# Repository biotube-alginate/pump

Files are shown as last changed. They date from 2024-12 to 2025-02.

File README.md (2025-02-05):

# Overview
This is the pump we used in BioTube for extruding alginate solution of high concentration (4%) and thus high viscocity. The noozle of the syringe can be directly vertically put into a Calcium solution bath without extra tubing connections.

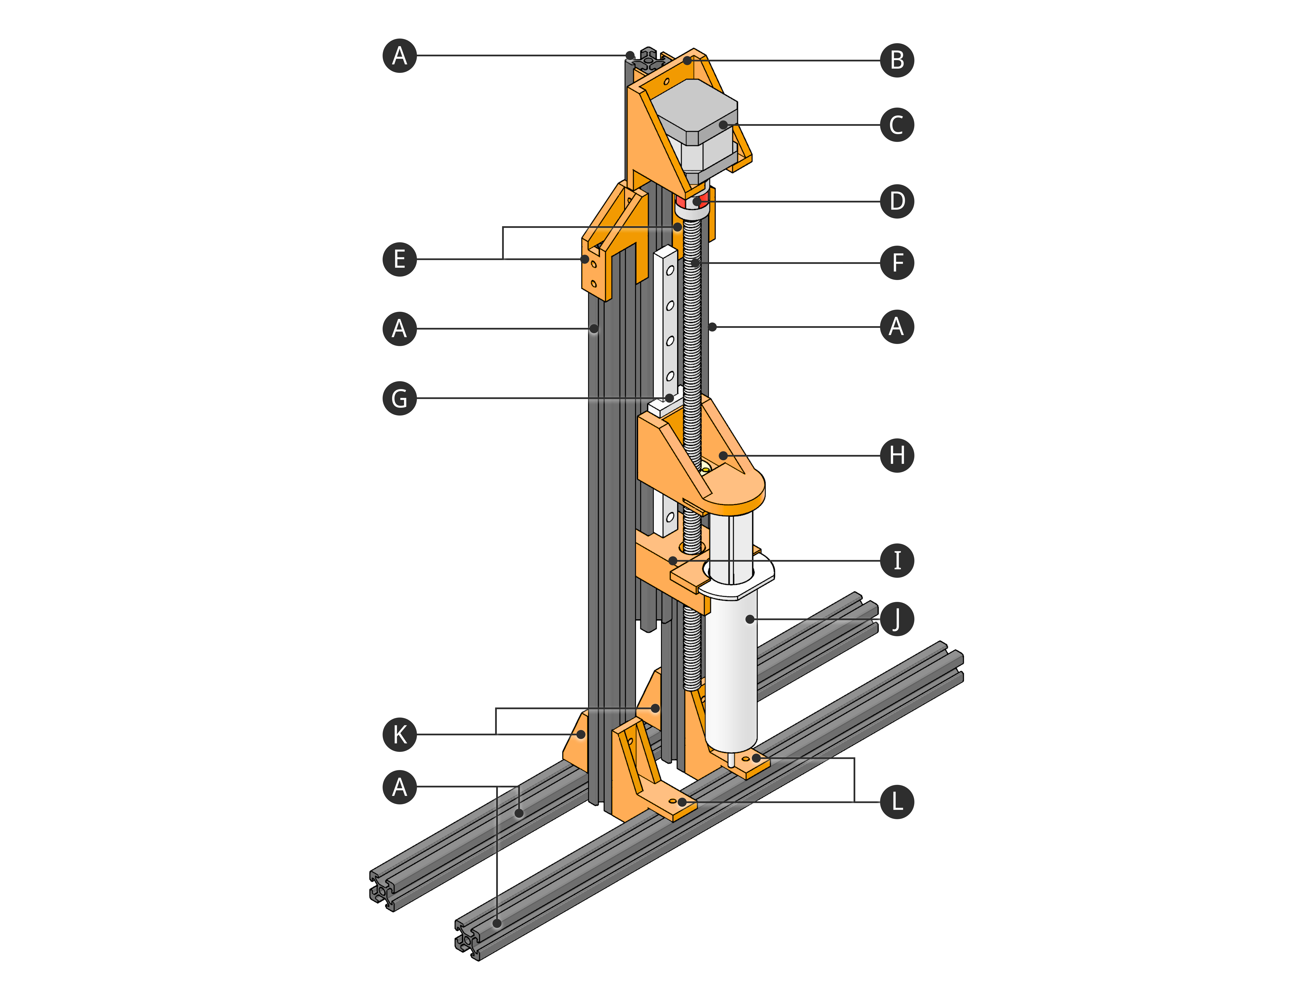
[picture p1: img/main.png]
Main Image


# BOM
> ⚠️ **Note**: The syringe holde in our design is specified for 60mL Easy Glide syringe, and syringes from different brand or of different volumes might vary in size and thus doesn't fit into our design.

| Part ID | Name       | Number     |Specification| Purchase Link/3D Print Model File | Cost |
|---------|------------|------------|------------|------------|------------|
| A       | Aluminum Extrusion |5|400mm T Slot| [Amazon](https://www.amazon.com/dp/B08Y8N7FD1?ref=nb_sb_ss_w_as-reorder_k0_1_13&amp=&crid=3VBMHCCEM3T1E&sprefix=aluminum%2Bextr&th=1) |$4.75/pc|
| B       | Motor Holder |1|-| [STL model](./model/pump/motor_holder.stl) |-|
| C       | Stepper Motor |1|STEPPERONLINE Nema 17 Bipolar 1.5A 42Ncm 42x42x38mm 1.8deg| [Amazon](https://www.amazon.com/dp/B0B38GX54H?ref=nb_sb_ss_w_as-reorder_k6_1_10&amp=&crid=38ALOK9A3HVA2&sprefix=stepper%2Bmo&th=1) |$10/pc|
| D       | Shaft Coupler |1|5mm to 8mm| [Amazon](https://www.amazon.com/Zeberoxyz-Aluminium-Diameter20mm-Length25mm-Motor%EF%BC%886-35x8mm%EF%BC%89/dp/B08QVK3MWH/ref=sr_1_3?crid=3KA69M92NF2WA&dib=eyJ2IjoiMSJ9.G8P_Ai-VgIKyJdhHRLNPaFbWD6G-bg2DOH26e_dJ_AqZjmpm3Kfxe9YSS5Xe-C9LNhXHVXSkyMVGvJhy3w7LEzOaFjR0_xhorvwDRA0BQtQm_o5658zIPECaxB-ZqSg8cTDzOxQJmyprdWSFRnvjLCkQS1sFaRJWD6SSXs8aNToE-gX1_88rdvoSFGOqlOt1210Tec3Ieczaz3KT_ldxUSrQaFBJubXfvxQNzg0u4AYk5PVZCS47C-DpApR4D3O-lKW9g2xUJenxwATmf2JsD0dofLakgFuol9Dsr3QFC7A.zFeMgHKedo4BgMLGxM52Td_1PwYd4vTPVeZjAgLir9o&dib_tag=se&keywords=coupler+cnc&qid=1731899614&s=industrial&sprefix=couplercnc%2Cindustrial%2C129&sr=1-3) |$6/pc|
| E       | Lift Holder |2|-| [STL model](./model/pump/lift_holder.stl) |-|
| F       | Lead Screw with T8 Brass Nut |1 |350mm Tr8X8 (8mm Lead)| [Amazon](https://www.amazon.com/350mm-Tr8X8-Printer-Machine-Thread/dp/B0981YH6X7/ref=sr_1_2_pp?crid=NEQGLEHW82GC&dib=eyJ2IjoiMSJ9.XdtkPX4h1YB3gFMo_YePmreEhNOOEAi2CmLBdDgSsTHB-3wYwS8haRcTaf3a1oEjmV1tqwPEirnk-9F1l8cae6sbfjtPA_5U_kjapQrdl2EYU7h5B_AtmhosBm2scBV2K1ft3Di68isoY8s2LcPTmuMYr2f1YLnbBJgMRdwr5bdYJAMjmTowmCOx6ZxLaEAsJHr9HI6Qugzwpb1oaoI3Nq0UQ5RLxOVberFVHpM9UnA.io_qYugfcRh9ozo9h-KOLmMDV_9QlyutgJxBOFQhjaI&dib_tag=se&keywords=lead%2Bscrew&qid=1731309743&sprefix=lead%2Bsc%2Caps%2C202&sr=8-2&th=1) |$6.5/pc|
| G       | Linear Rail Guide |1|200mm MGN12H| [Amazon](https://www.amazon.com/ReliaBot-Linear-Carriage-Printer-Machine/dp/B07B4F2G48/ref=sr_1_4_pp?crid=3HSZ4GF0LXEF2&dib=eyJ2IjoiMSJ9.xv2mApy6OXeImp8zS-IY6t70tfCA4BcpTICYGr9J_tMtcL_7kACzuE-CrbZeUZvERJZC2Z9pb4-slgjQzCD1b9FKAKP6sbQCfrlgxB-V7TV8RjUyN2DV_Y4rUgEaULpjn2-HMRz2njCQ_zqqqx1MmIzFBtJzp1PTixS84pacS87l1szy-a8_WwY_WHtvnWcDmblIF_af1kneVuAi60JAlt2LCVxMGwlcdZMn1fLJB-Fg02CGcyWACvvMhueOOeiiVw9yHgw-puRPskDnv_H6uXJNlZameKzSuGZgbKYkeGo.Iz3TFtNkxApBWyeGzGlUHMSDNU7jYEYcUuqq0SmM628&dib_tag=se&keywords=linear%2Brail&qid=1731900294&s=industrial&sprefix=linear%2B%2Cindustrial%2C165&sr=1-4&th=1) |$18.59/pc|
| H       | Syringe Pusher |1|-| [STL model](./model/pump/syringe_pusher.stl) |-|
| I       | Syringe Holder |1|-| [STL model](./model/pump/syring_holder.stl) |-|
| J       | Syringe |1| Easy Glide 60mL| [Amazon](https://www.amazon.com/Global-Medical-Products-60cc-Syringes/dp/B07K1LR8NJ/ref=sr_1_3?crid=1YVAX7296ZPDI&dib=eyJ2IjoiMSJ9.sfwbnAiL-UMPtVgMlCeXilNhKokHq4WBHPKrefE8LbbkilqJLqJi-5AKSXLQeCXbu-kI5THbe7prRCoctJcOJ9-DCX-ehh51RlSZ1OutUZDy7vUJt-dTMZ6aoiYvSOxRfpAf92elrvULm3Qy-fMeMxpjHPBO5WJk0idDvyzXj0Pb6YnnG1KoWUMVN-8-aS1nKdCfEYkUIyZTzatJBi-OOxDxGrEoBUb29GUQJsJnzLafz0Bsb8g9hWv-jRiWaraHYRP6zdkkpFFN3HbS7DA_yWBcpNNyavusk0DvjQTpgoQ.uGhV05sAeG0f6NwzT-c5rWgmFhGA433Bso1aP3aBk9E&dib_tag=se&keywords=60+ml+syringe+easy+glide&qid=1731900449&s=industrial&sprefix=60+ml+syringe+easy+glid%2Cindustrial%2C134&sr=1-3) |$0.9/pc|
| K       | Base Fix |2|-| [STL model](./model/pump/base_fix.stl) |-|
| L       | Base Fix_2 |2|-| [STL model](./model/pump/base_fix_2.stl) |-|

- T-Nuts used: https://www.amazon.com/Hulless-Sliding-Fastener-Aluminum-Accessories/dp/B08NZMD2BJ

# Assembly
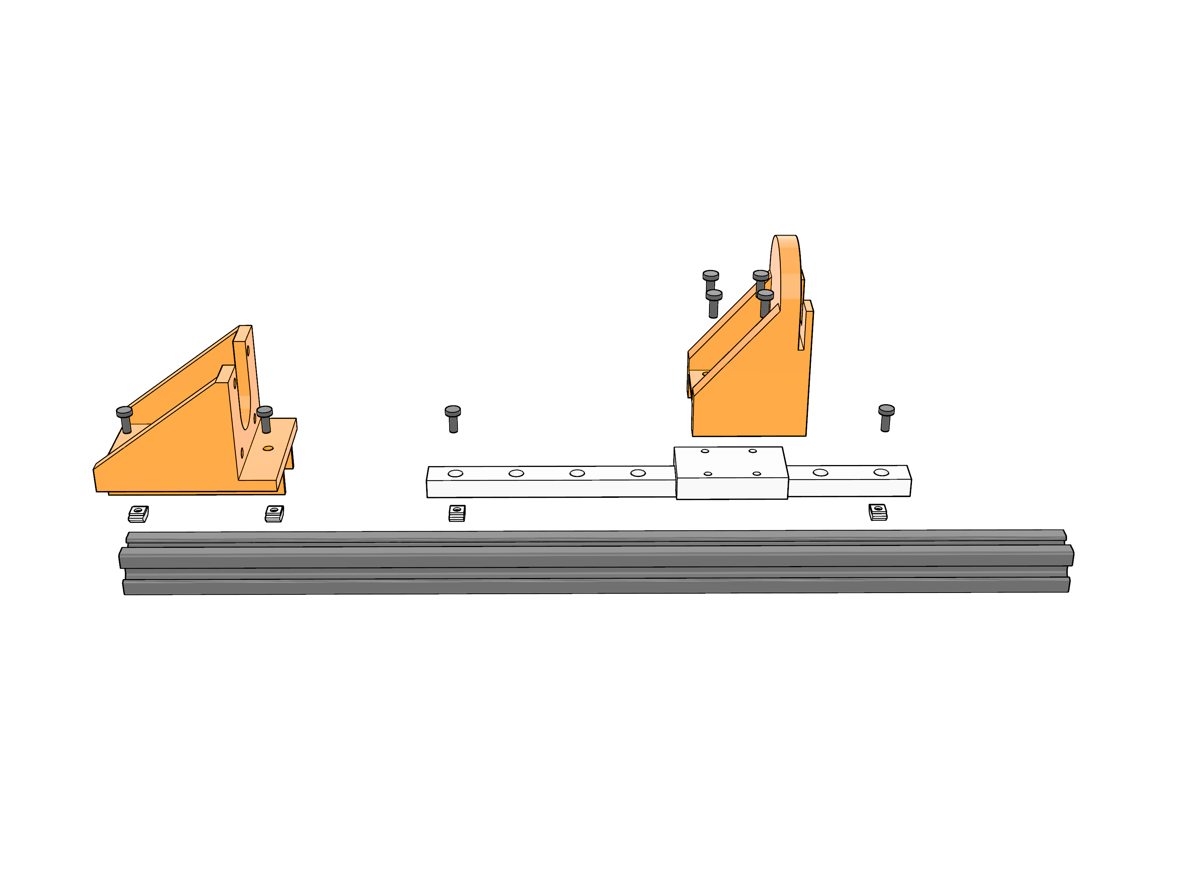
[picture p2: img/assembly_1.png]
assembly_1

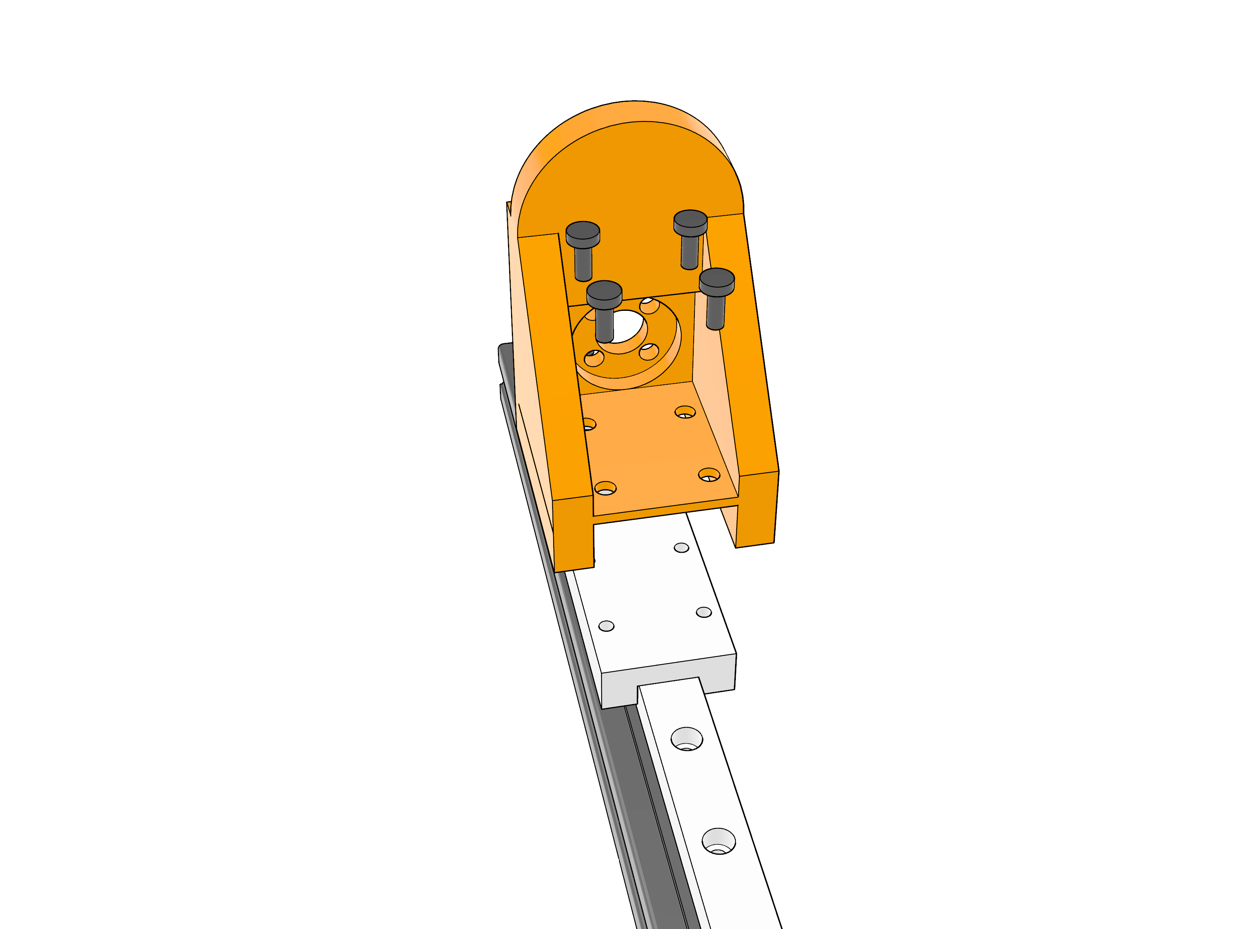
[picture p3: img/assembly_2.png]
assembly_2

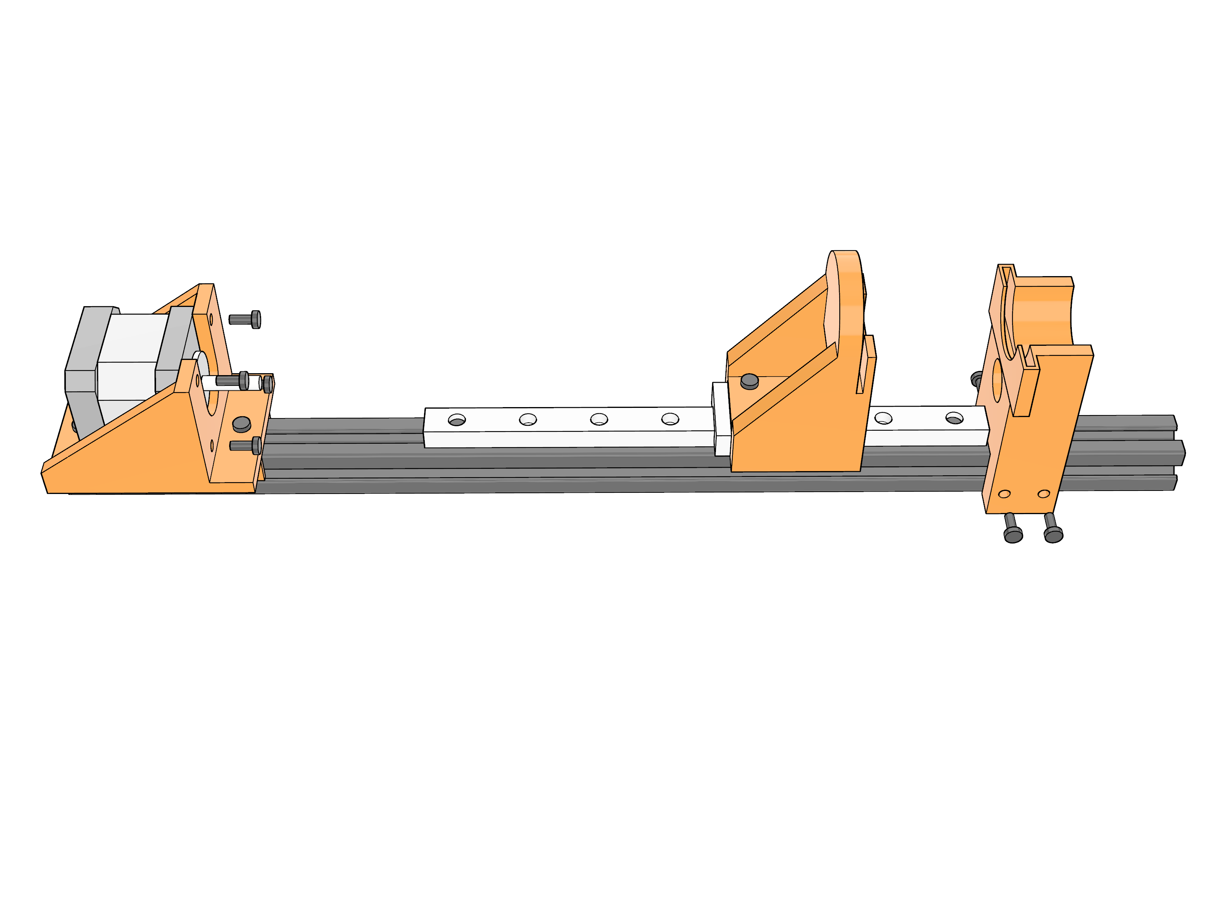
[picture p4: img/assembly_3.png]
assembly_3

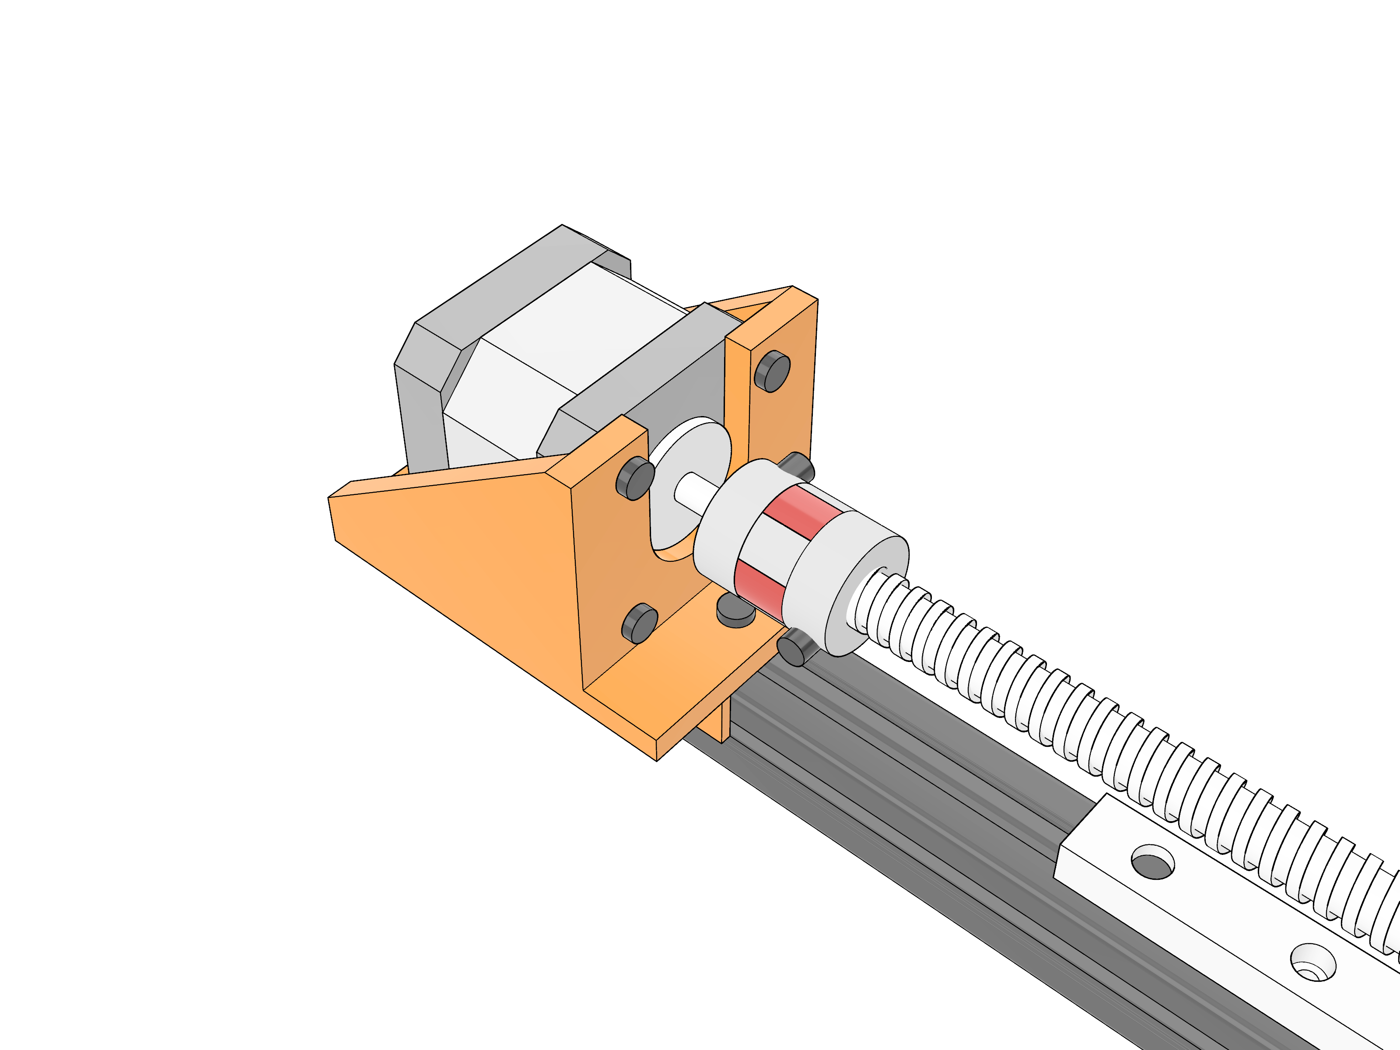
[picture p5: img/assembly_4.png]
assembly_4

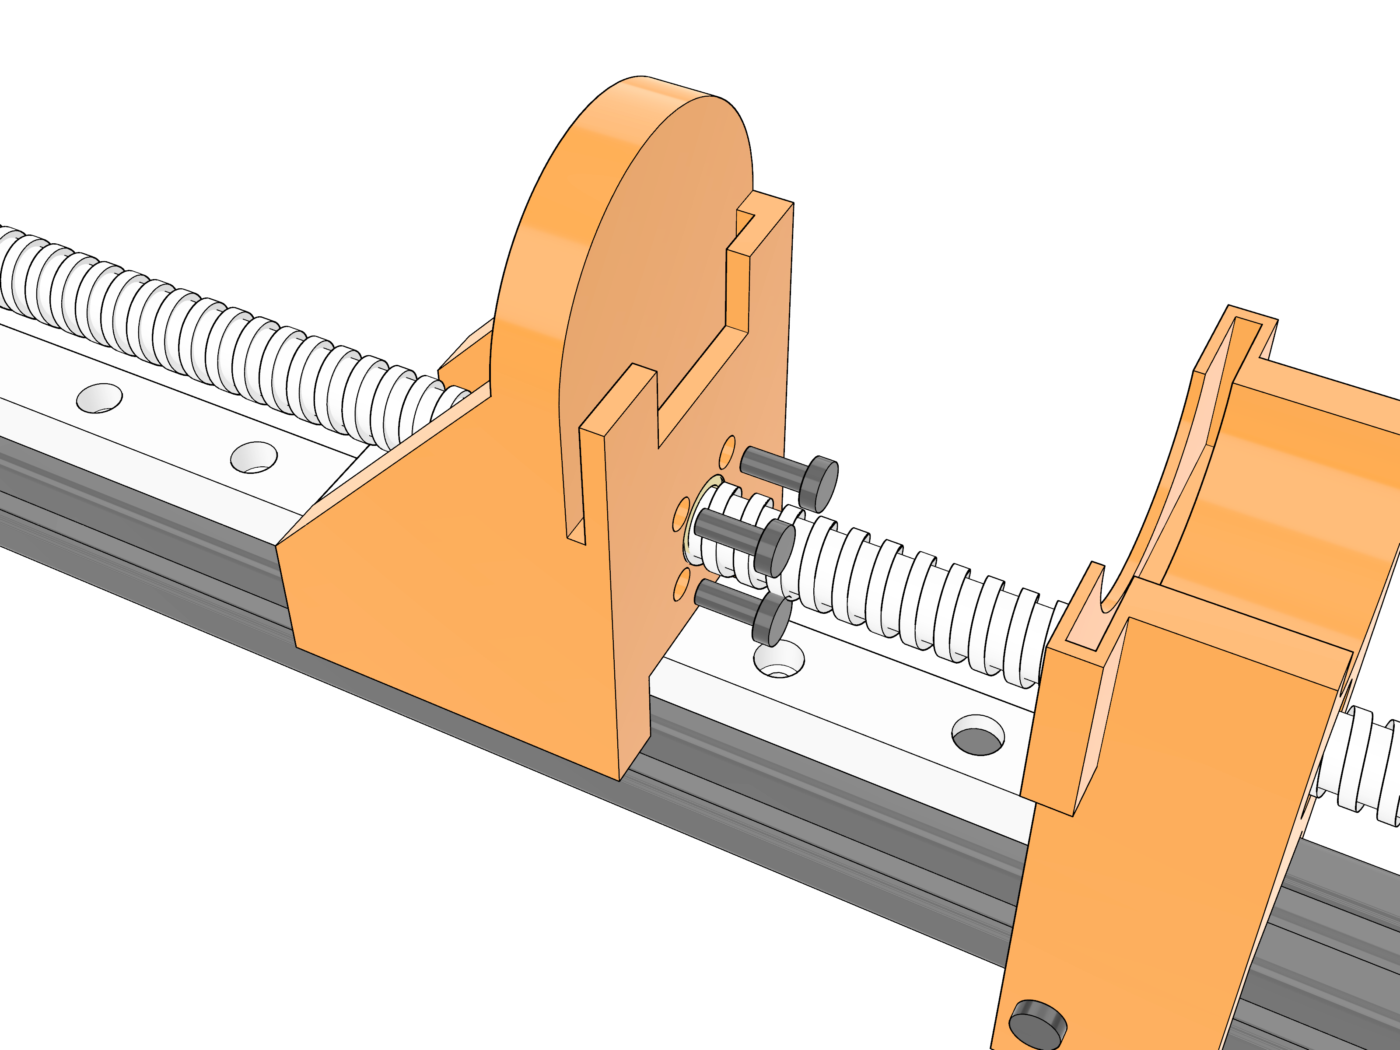
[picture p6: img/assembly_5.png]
assembly_5

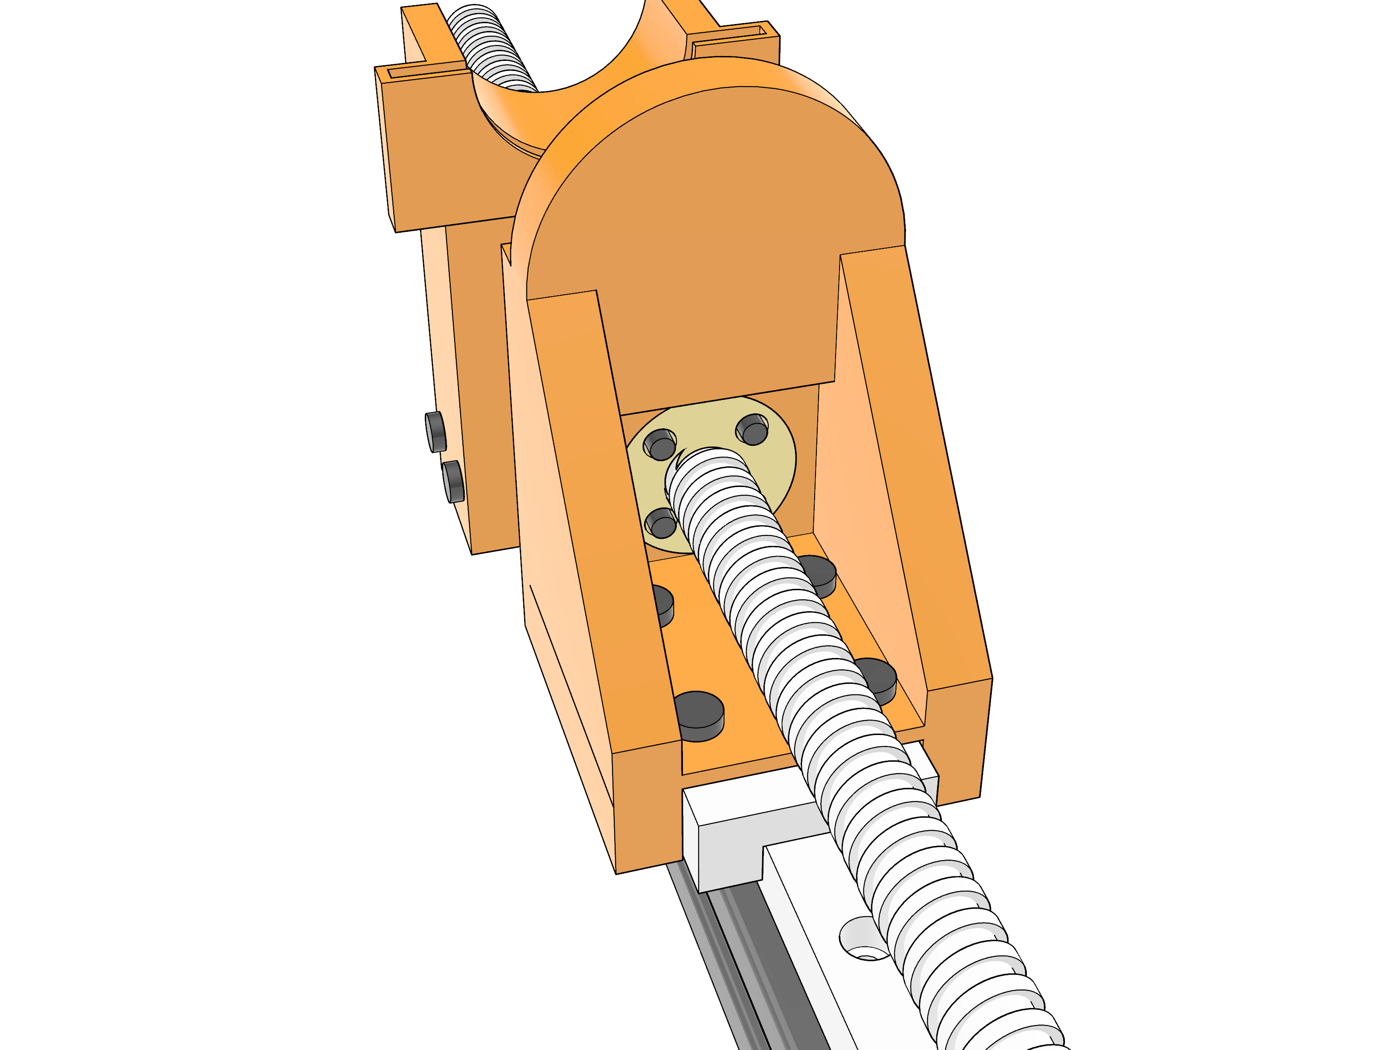
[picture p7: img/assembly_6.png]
assembly_6


# Hardware
We used [Adafruit TB6612](https://www.adafruit.com/product/2448?gad_source=1&gclid=CjwKCAiA34S7BhAtEiwACZzv4feKOWty9u_dhpJHnMaGh85bf2fnYS228pUAWPnXRmB9vD5l0R1kcBoCeTUQAvD_BwE) as the stepper motor driver board and Arduino Uno as the micro-controller. Detailed assembly and wiring setup tutorials can be found [here](https://learn.adafruit.com/adafruit-tb6612-h-bridge-dc-stepper-motor-driver-breakout). 

# Spooling System
Using the syringe pump, we can further build a spooling system to wet-spin long fibers.
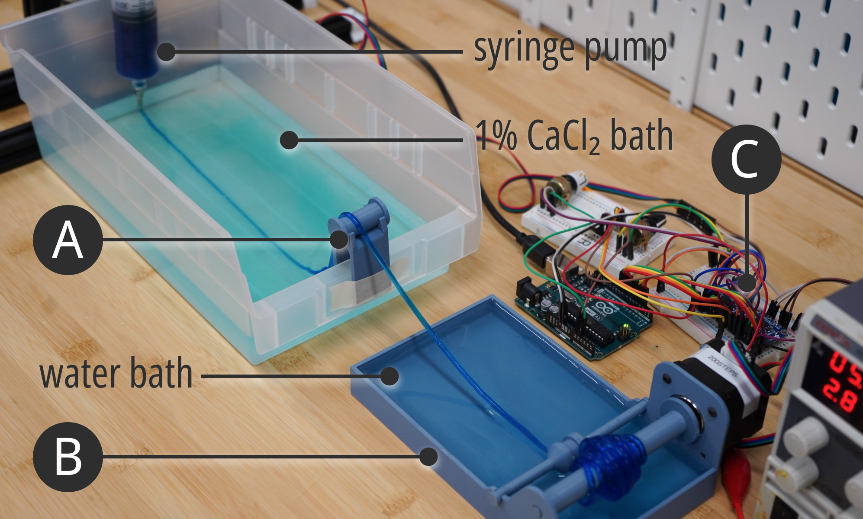
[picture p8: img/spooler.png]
spooler

| Part ID | Name  | Purchase Link/3D Print Model File | Notes |
|---------|-----------|------------|------------|
| A       | Transfer guide | [roller STL model](./model/spool/trans_roller.stl) and [stand STL model](./model/spool/trans_stand.stl)|two parts snap fit together, stand on the edge of the calcium bath.|
| B       | Spooler | [dish STL model](./model/spool/spool_dish.stl), [guide STL model](./model/spool/spool_guide.stl), and [roller STL model](./model/spool/spool_roller.stl)|spool guide snap fit to the dish, the roller friction fit to the stepper motor(STEPPERONLINE Nema 17 Bipolar), and the motor is fixed with M3 screws onto the base dish.|
| C       | Hardware | [stepper motor](https://www.amazon.com/dp/B0B38GX54H?ref=nb_sb_ss_w_as-reorder_k6_1_10&amp=&crid=38ALOK9A3HVA2&sprefix=stepper+mo&th=1), [Adafruit TB6612](https://www.adafruit.com/product/2448?gad_source=1&gclid=CjwKCAiA34S7BhAtEiwACZzv4feKOWty9u_dhpJHnMaGh85bf2fnYS228pUAWPnXRmB9vD5l0R1kcBoCeTUQAvD_BwE), and [Arduino Uno](https://www.amazon.com/Arduino-A000066-ARDUINO-UNO-R3/dp/B008GRTSV6/ref=sr_1_1_sspa?crid=3EVBEBEY5WUFD&dib=eyJ2IjoiMSJ9.MazmhFfn-DF8W5oyX_S-tDFAqLRDaMJSkroaZhdQMdgePys4UzrERZgaxu0RHrmwh6oVgxMiZ5PykFPY45Zvj87Nho46YM6UFmLyyZZjAn0L6t074YVOiWT-Q1EMX25k9gRe8ueEZ7A3kq8jP-jDkeuLtxGGCNdmPTliHHHvkVxqbvugIL-X0fECy0TzHxMwYFdukx7wd_svuEpTiAROAJ-aajf0YsN01CJUSs8xPC3EDYmW-gRf4Y5dC6FYkEryJn5V-s3US-daFTKSAhzqNwH3oRdLt56vptFPsIZFdq8.i5OoYhdnTQZC547sfhsutnHWYddfm_C7XG3OLTD-EuQ&dib_tag=se&keywords=arduino+uno&qid=1734476558&s=industrial&sprefix=arduino+uno%2Cindustrial%2C164&sr=1-1-spons&sp_csd=d2lkZ2V0TmFtZT1zcF9hdGY&psc=1)|Reference [tutorial](https://learn.adafruit.com/adafruit-tb6612-h-bridge-dc-stepper-motor-driver-breakout) for TB6612 wiring. We further used two potentiometers to tune the extrusion speed of the syringe pump and the spooling speed of the spooler on the fly so they can match.|

# Open Source
Our design is licensed under a Creative Commons Attribution-NonCommercial-ShareAlike 4.0 International (CC BY-NC-SA 4.0) https://creativecommons.org/licenses/by-nc-sa/4.0/.

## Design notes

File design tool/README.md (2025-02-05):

### Grasshopper Design Tool for Generating 3D Printed Reshape Mold for Alginate Fibers
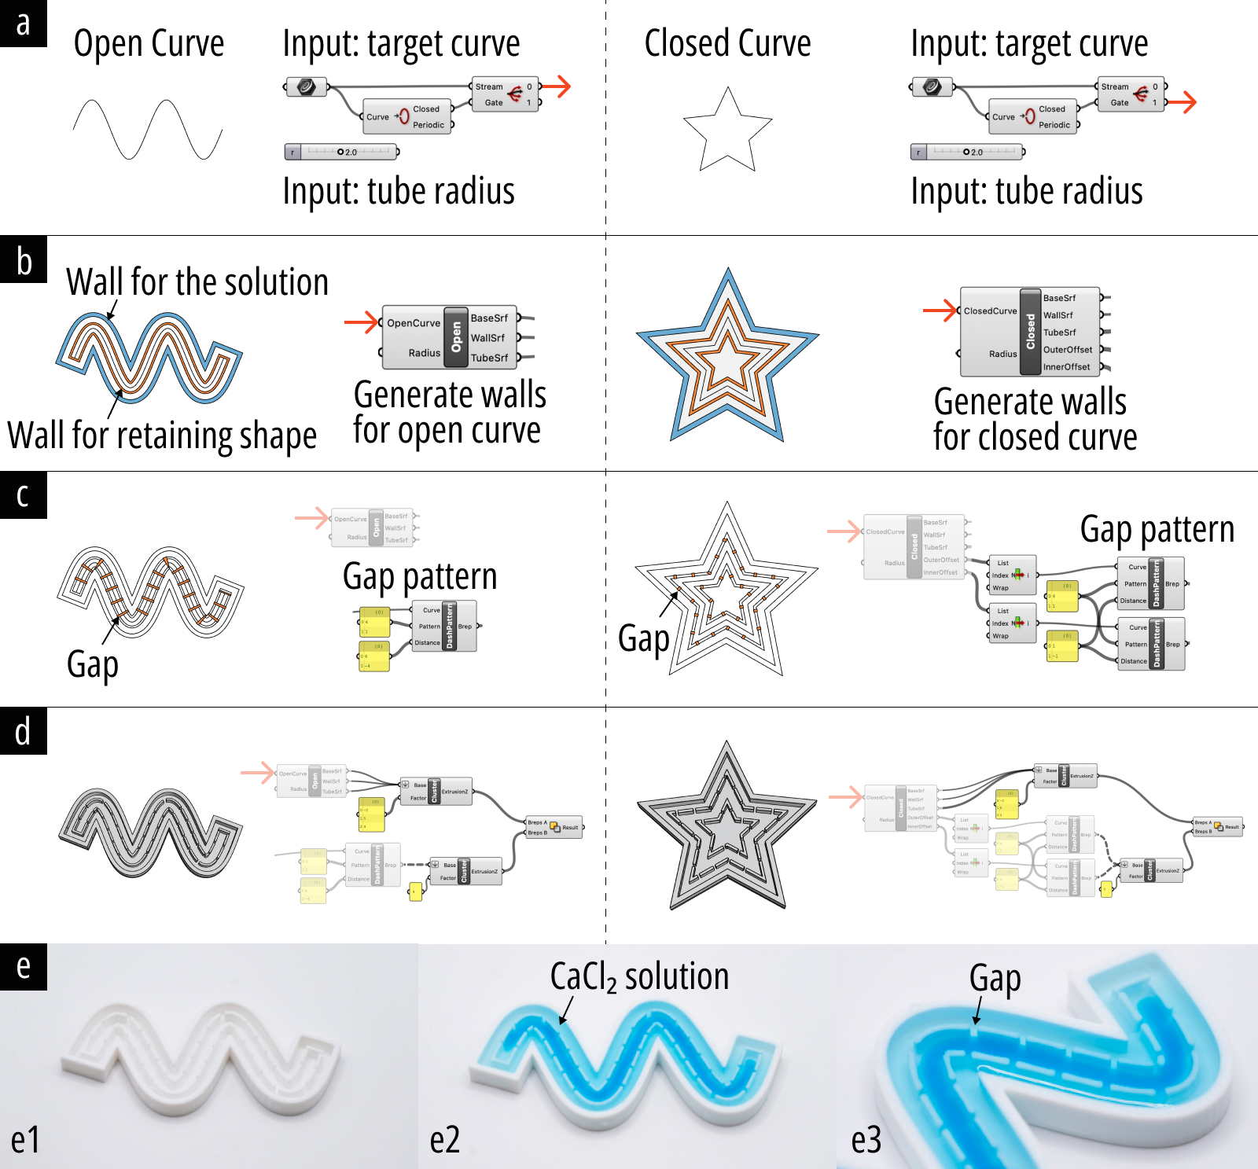
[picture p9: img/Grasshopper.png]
design tool image

Design tool for the mold to form alginate fibers into 2D geometries using the reshaping crosslinking process. (a) Users can input 2D curves and set the desired tubular alginate radius. (b) Walls are generated to retain the alginate shape and contain the $ \text{CaCl}_2 $ solution. (c) Gaps in the walls are created to allow the $ \text{CaCl}_2 $ solution to replenish calcium ions inside the inner walls, ensuring consistent crosslinking of the alginate fibers. (d) The final mold is generated and can be exported for 3D printing. (e) Printed mold and an example of usage.

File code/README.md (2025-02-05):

### Arduino Code for Driving Stepper Motor

We used a Usongshine Nema 17 stepper motor, driven by Adafruit's TB6612 motor driver breakout board. For hardware assembly, we followed [this Adafruit tutorial](https://learn.adafruit.com/adafruit-tb6612-h-bridge-dc-stepper-motor-driver-breakout/using-stepper-motors). The Arduino code was modified to enable the stepper motor to accept RPM values as floating-point numbers.

- **`motor_control_single`**: Arduino code for controlling a single stepper motor, suitable for the main syringe pump setup described [here](../README.md)). In our primary setup, we used a fixed motor speed. However, the code also provides an option to read an analog input from pin A0 (e.g., connected to a voltage divider circuit with a potentiometer) for real-time motor speed adjustment.

- **`motor_control`**: similar to **`motor_control_single`** but offers control over to three stepper motors.

- **`motor_control_length`**: Similar to **`motor_control_single`** (for continuous fiber spinning), but with the added ability to specify the desired fiber length.

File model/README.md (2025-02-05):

### 3D Print Model Files

- **`optical`**: 3D Print Files for Alginate Optical Fiber Connection Parts
- **`pump`**: 3D Print Files for the Syringe Pump Parts
- **`roller`**: 3D Print Files for the Roller
- **`spool`**: 3D Print Files for the Spooling System

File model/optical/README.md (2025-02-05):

### 3D Print Files for Alginate Optical Fiber Connection Parts

These files provide 3D print connection components for using alginate as an optical fiber. The purpose of each part is detailed below:

- **`light_cap.stl`**: The connector between the alginate fiber and a laser pointer (Yiwu Zhangkun Electronic Commerce Co., Ltd).

- **`light_sensor_cap.stl`**: The connector between the alginate fiber and the photoresistance sensor (EBOOT).

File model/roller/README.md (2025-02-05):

###  Roller STL Files for 3D Print

The STL files in the `roller` directory are derived from a 3D model originally published on Thingiverse: [Original Roller Design by norm8332 on Thingiverse](https://www.thingiverse.com/thing:1721305). We have modified the wheel component of the original design to better accommodate the removal of the core from alginate tubes.

The original roller design is licensed under the [Creative Commons Attribution-NonCommercial-ShareAlike (CC BY-NC-SA)](https://creativecommons.org/licenses/by-nc-sa/4.0/) license. Our modified versions are distributed under the same license.



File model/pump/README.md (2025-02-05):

### 3D Print Files for the Syringe Pump

Parts usage specified [here](../../README.md).

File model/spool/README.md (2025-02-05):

### 3D Print Files for the Spooling System

Parts usage specified [here](../../README.md).

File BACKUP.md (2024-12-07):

# Overview
This is the pump we used in BioTube for extruding alginate solution of high concentration (4%) and thus high viscocity. The noozle of the syringe can be directly vertically put into a Calcium solution bath without extra tubing connections.

Main Image

# BOM
> ⚠️ **Note**: The syringe holde in our design is specified for 60mL Easy Glide syringe, and syringes from different brand or of different volumes might vary in size and thus doesn't fit into our design.

| Part ID | Name       | Number     |Specification| Purchase Link/3D Print Model File | Cost |
|---------|------------|------------|------------|------------|------------|
| A       | Aluminum Extrusion |5|400mm T Slot| [Amazon](https://www.amazon.com/dp/B08Y8N7FD1?ref=nb_sb_ss_w_as-reorder_k0_1_13&amp=&crid=3VBMHCCEM3T1E&sprefix=aluminum%2Bextr&th=1) |$4.75/pc|
| B       | Motor Holder |1|-| [STL model](/model/motor_holder.stl) |-|
| C       | Stepper Motor |1|STEPPERONLINE Nema 17 Bipolar 1.5A 42Ncm 42x42x38mm 1.8deg| [Amazon](https://www.amazon.com/dp/B0B38GX54H?ref=nb_sb_ss_w_as-reorder_k6_1_10&amp=&crid=38ALOK9A3HVA2&sprefix=stepper%2Bmo&th=1) |$10/pc|
| D       | Shaft Coupler |1|5mm to 8mm| [Amazon](https://www.amazon.com/Zeberoxyz-Aluminium-Diameter20mm-Length25mm-Motor%EF%BC%886-35x8mm%EF%BC%89/dp/B08QVK3MWH/ref=sr_1_3?crid=3KA69M92NF2WA&dib=eyJ2IjoiMSJ9.G8P_Ai-VgIKyJdhHRLNPaFbWD6G-bg2DOH26e_dJ_AqZjmpm3Kfxe9YSS5Xe-C9LNhXHVXSkyMVGvJhy3w7LEzOaFjR0_xhorvwDRA0BQtQm_o5658zIPECaxB-ZqSg8cTDzOxQJmyprdWSFRnvjLCkQS1sFaRJWD6SSXs8aNToE-gX1_88rdvoSFGOqlOt1210Tec3Ieczaz3KT_ldxUSrQaFBJubXfvxQNzg0u4AYk5PVZCS47C-DpApR4D3O-lKW9g2xUJenxwATmf2JsD0dofLakgFuol9Dsr3QFC7A.zFeMgHKedo4BgMLGxM52Td_1PwYd4vTPVeZjAgLir9o&dib_tag=se&keywords=coupler+cnc&qid=1731899614&s=industrial&sprefix=couplercnc%2Cindustrial%2C129&sr=1-3) |$6/pc|
| E       | Lift Holder |2|-| [STL model](/model/lift_holder.stl) |-|
| F       | Lead Screw with T8 Brass Nut |1 |350mm Tr8X8 (8mm Lead)| [Amazon](https://www.amazon.com/350mm-Tr8X8-Printer-Machine-Thread/dp/B0981YH6X7/ref=sr_1_2_pp?crid=NEQGLEHW82GC&dib=eyJ2IjoiMSJ9.XdtkPX4h1YB3gFMo_YePmreEhNOOEAi2CmLBdDgSsTHB-3wYwS8haRcTaf3a1oEjmV1tqwPEirnk-9F1l8cae6sbfjtPA_5U_kjapQrdl2EYU7h5B_AtmhosBm2scBV2K1ft3Di68isoY8s2LcPTmuMYr2f1YLnbBJgMRdwr5bdYJAMjmTowmCOx6ZxLaEAsJHr9HI6Qugzwpb1oaoI3Nq0UQ5RLxOVberFVHpM9UnA.io_qYugfcRh9ozo9h-KOLmMDV_9QlyutgJxBOFQhjaI&dib_tag=se&keywords=lead%2Bscrew&qid=1731309743&sprefix=lead%2Bsc%2Caps%2C202&sr=8-2&th=1) |$6.5/pc|
| G       | Linear Rail Guide |1|200mm MGN12H| [Amazon](https://www.amazon.com/ReliaBot-Linear-Carriage-Printer-Machine/dp/B07B4F2G48/ref=sr_1_4_pp?crid=3HSZ4GF0LXEF2&dib=eyJ2IjoiMSJ9.xv2mApy6OXeImp8zS-IY6t70tfCA4BcpTICYGr9J_tMtcL_7kACzuE-CrbZeUZvERJZC2Z9pb4-slgjQzCD1b9FKAKP6sbQCfrlgxB-V7TV8RjUyN2DV_Y4rUgEaULpjn2-HMRz2njCQ_zqqqx1MmIzFBtJzp1PTixS84pacS87l1szy-a8_WwY_WHtvnWcDmblIF_af1kneVuAi60JAlt2LCVxMGwlcdZMn1fLJB-Fg02CGcyWACvvMhueOOeiiVw9yHgw-puRPskDnv_H6uXJNlZameKzSuGZgbKYkeGo.Iz3TFtNkxApBWyeGzGlUHMSDNU7jYEYcUuqq0SmM628&dib_tag=se&keywords=linear%2Brail&qid=1731900294&s=industrial&sprefix=linear%2B%2Cindustrial%2C165&sr=1-4&th=1) |$18.59/pc|
| H       | Syringe Pusher |1|-| [STL model](/model/syringe_pusher.stl) |-|
| I       | Syringe Holder |1|-| [STL model](/model/syring_holder.stl) |-|
| J       | Syringe |1| Easy Glide 60mL| [Amazon](https://www.amazon.com/Global-Medical-Products-60cc-Syringes/dp/B07K1LR8NJ/ref=sr_1_3?crid=1YVAX7296ZPDI&dib=eyJ2IjoiMSJ9.sfwbnAiL-UMPtVgMlCeXilNhKokHq4WBHPKrefE8LbbkilqJLqJi-5AKSXLQeCXbu-kI5THbe7prRCoctJcOJ9-DCX-ehh51RlSZ1OutUZDy7vUJt-dTMZ6aoiYvSOxRfpAf92elrvULm3Qy-fMeMxpjHPBO5WJk0idDvyzXj0Pb6YnnG1KoWUMVN-8-aS1nKdCfEYkUIyZTzatJBi-OOxDxGrEoBUb29GUQJsJnzLafz0Bsb8g9hWv-jRiWaraHYRP6zdkkpFFN3HbS7DA_yWBcpNNyavusk0DvjQTpgoQ.uGhV05sAeG0f6NwzT-c5rWgmFhGA433Bso1aP3aBk9E&dib_tag=se&keywords=60+ml+syringe+easy+glide&qid=1731900449&s=industrial&sprefix=60+ml+syringe+easy+glid%2Cindustrial%2C134&sr=1-3) |$0.9/pc|
| K       | Base Fix |2|-| [STL model](/model/base_fix.stl) |-|
| L       | Base Fix_2 |2|-| [STL model](/model/base_fix_2.stl) |-|

- tnut: https://www.amazon.com/Hulless-Sliding-Fastener-Aluminum-Accessories/dp/B08NZMD2BJ

# Assembly
assembly_1
assembly_2
assembly_3
assembly_4
assembly_5
assembly_6

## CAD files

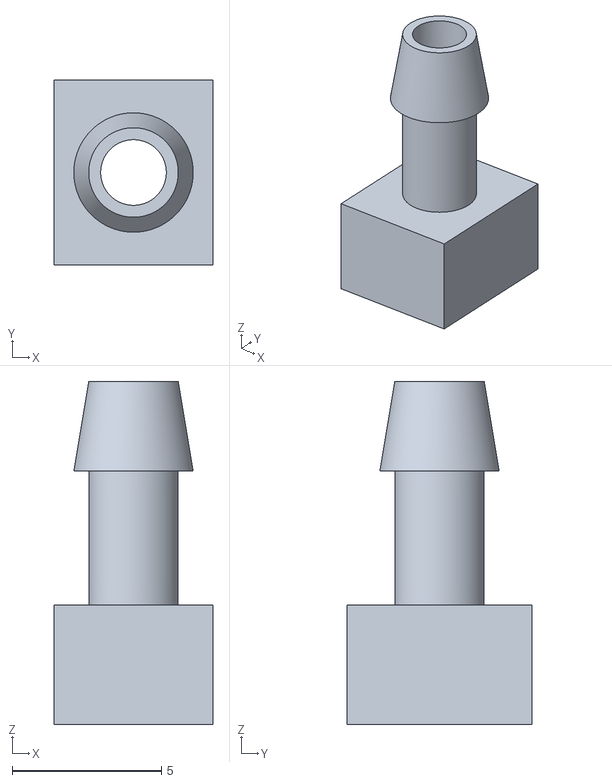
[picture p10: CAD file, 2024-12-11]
model/optical/light_sensor_cap.stl
5.33 x 6.20 x 11.5

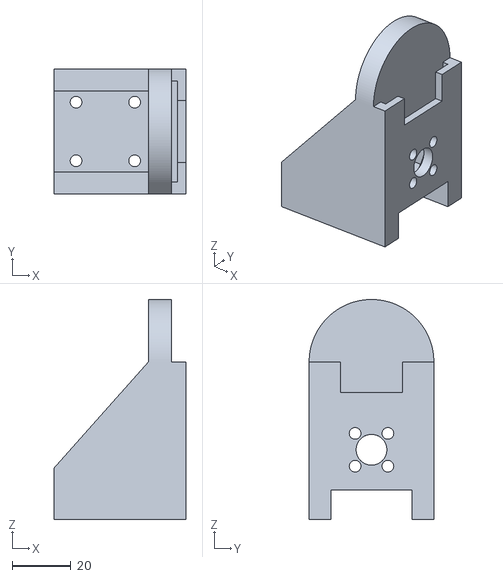
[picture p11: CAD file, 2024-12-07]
model/pump/syringe_pusher.stl
45.0 x 42.6 x 75.1

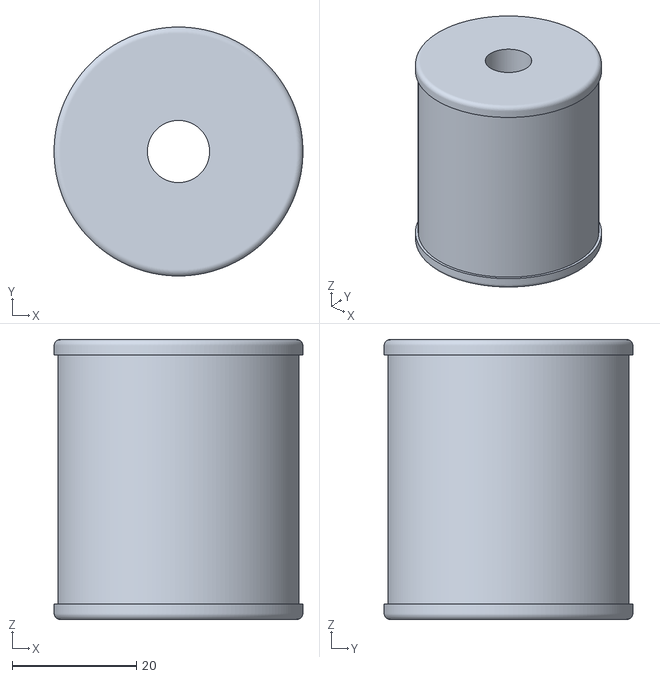
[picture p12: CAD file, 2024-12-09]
model/roller/wheel.stl
40.0 x 40.0 x 45.0

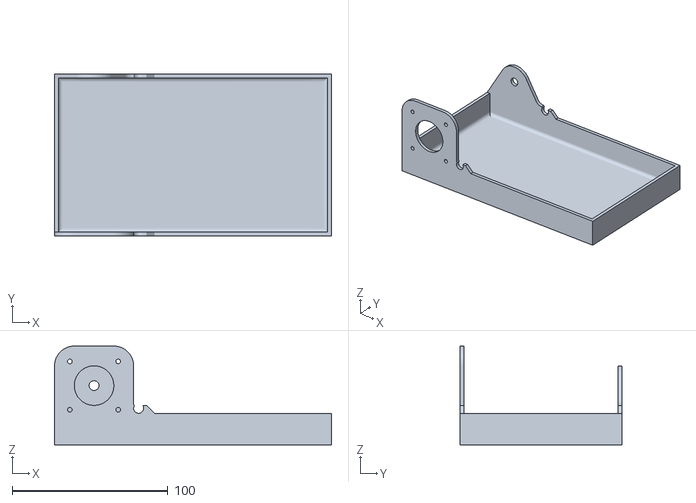
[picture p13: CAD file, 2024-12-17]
model/spool/spool_dish.stl
177.8 x 104.1 x 63.5

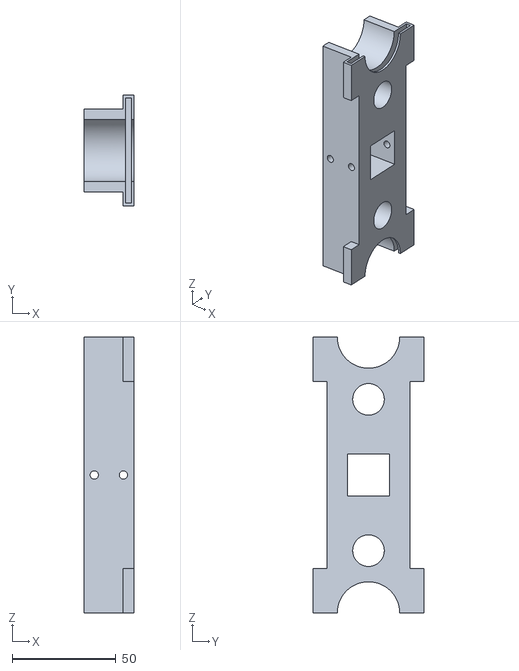
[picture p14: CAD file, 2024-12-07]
model/pump/syring_holder_dual.stl
24.1 x 53.5 x 132.8

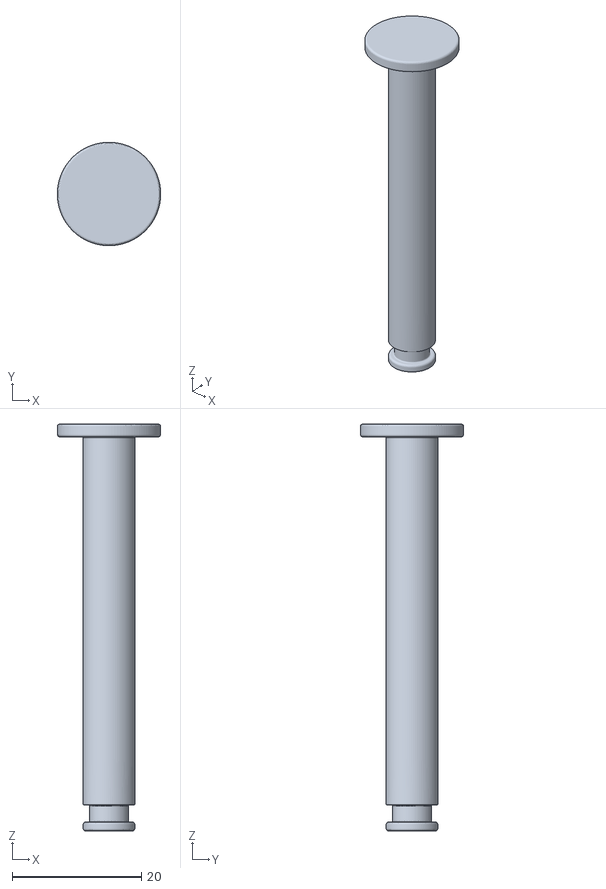
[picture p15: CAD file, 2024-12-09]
model/roller/pin.stl
16.0 x 16.0 x 63.0

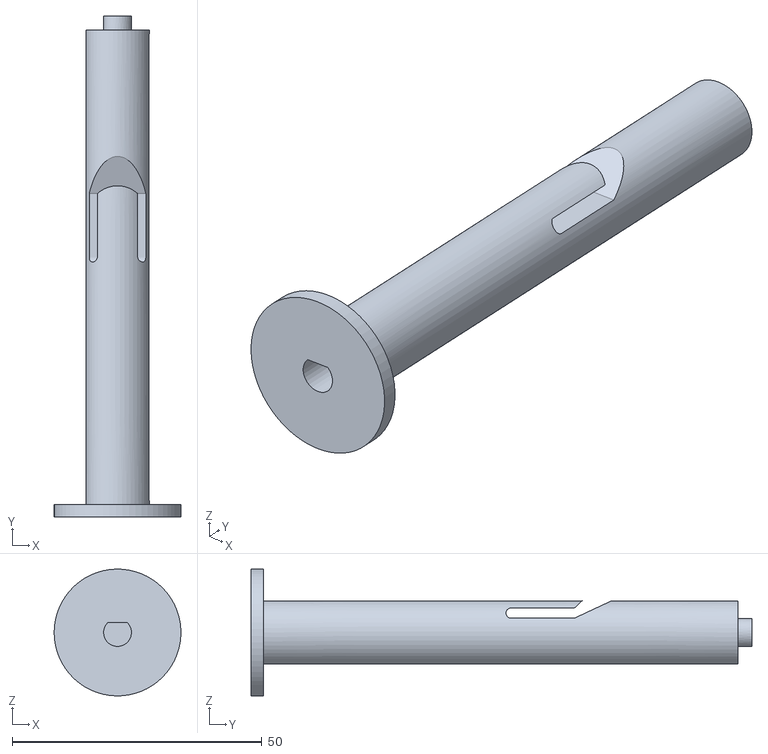
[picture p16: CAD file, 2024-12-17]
model/spool/spool_roller.stl
25.4 x 100.3 x 25.4

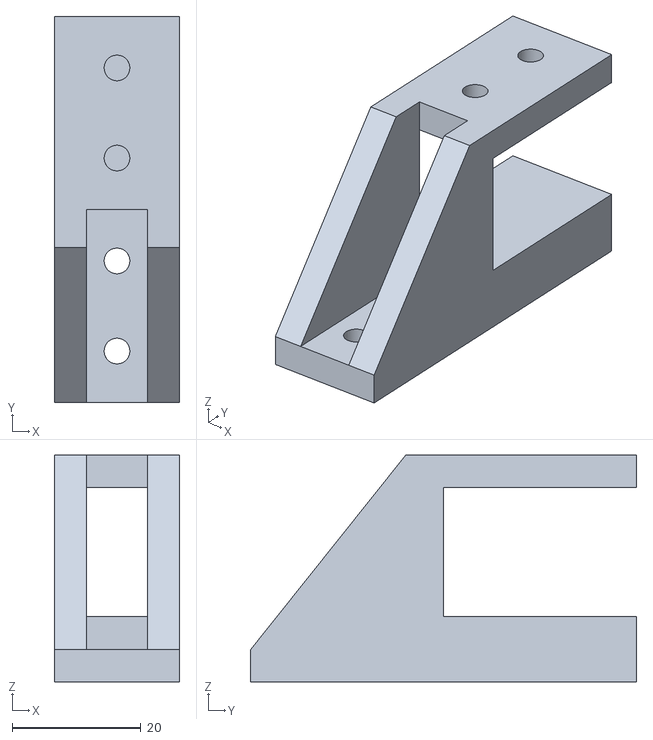
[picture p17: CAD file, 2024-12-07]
model/pump/lift_holder.stl
19.5 x 60.0 x 35.2

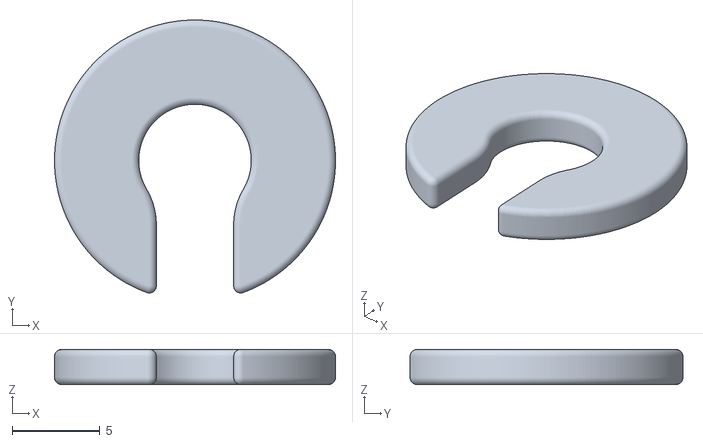
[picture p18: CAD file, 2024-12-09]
model/roller/clip.stl
16.0 x 15.5 x 2.00

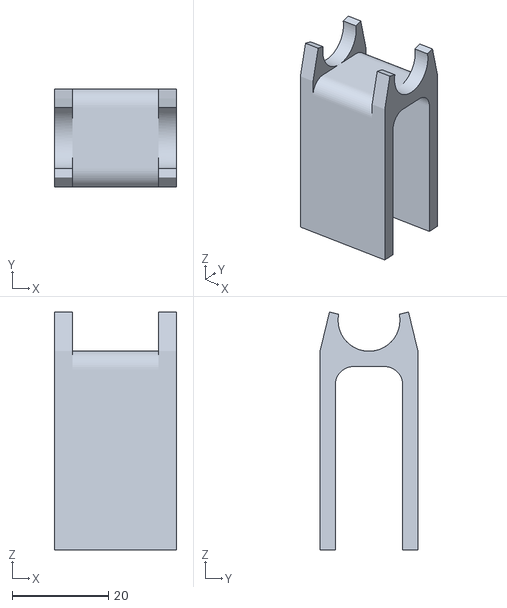
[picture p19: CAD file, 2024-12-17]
model/spool/trans_stand.stl
25.4 x 20.3 x 49.4

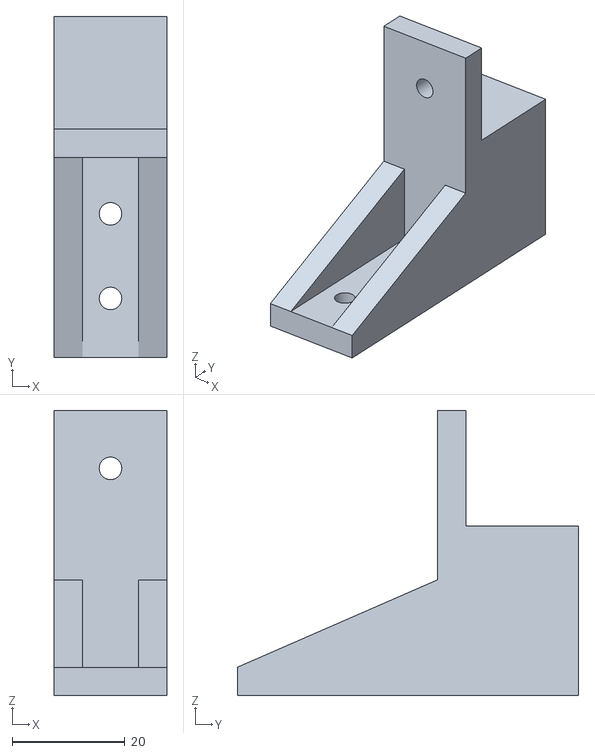
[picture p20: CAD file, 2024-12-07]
model/pump/base_fix_2.stl
20.0 x 60.5 x 50.5

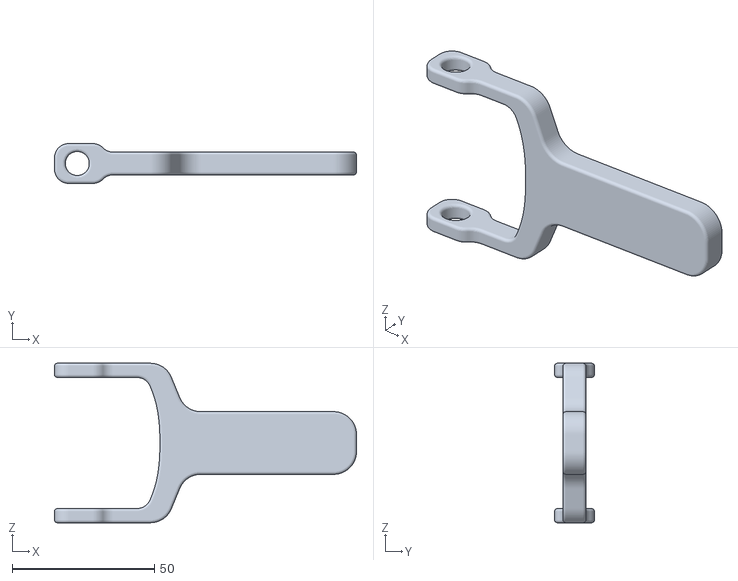
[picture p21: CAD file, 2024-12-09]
model/roller/handle.stl
106.0 x 14.0 x 56.0

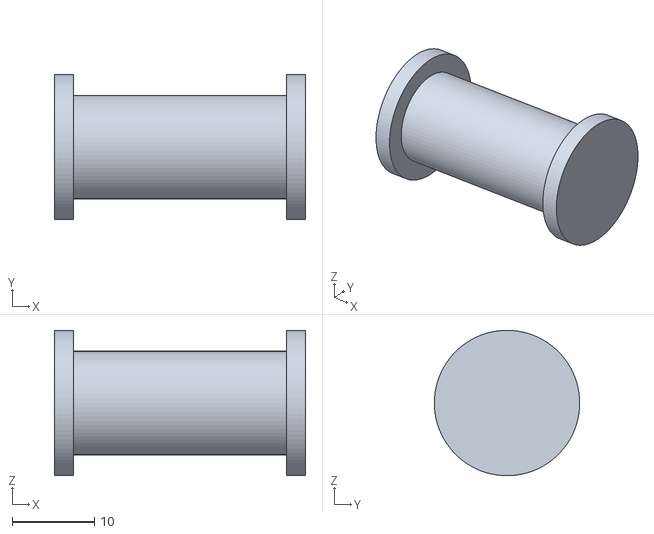
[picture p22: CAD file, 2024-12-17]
model/spool/trans_roller.stl
30.5 x 17.7 x 17.7

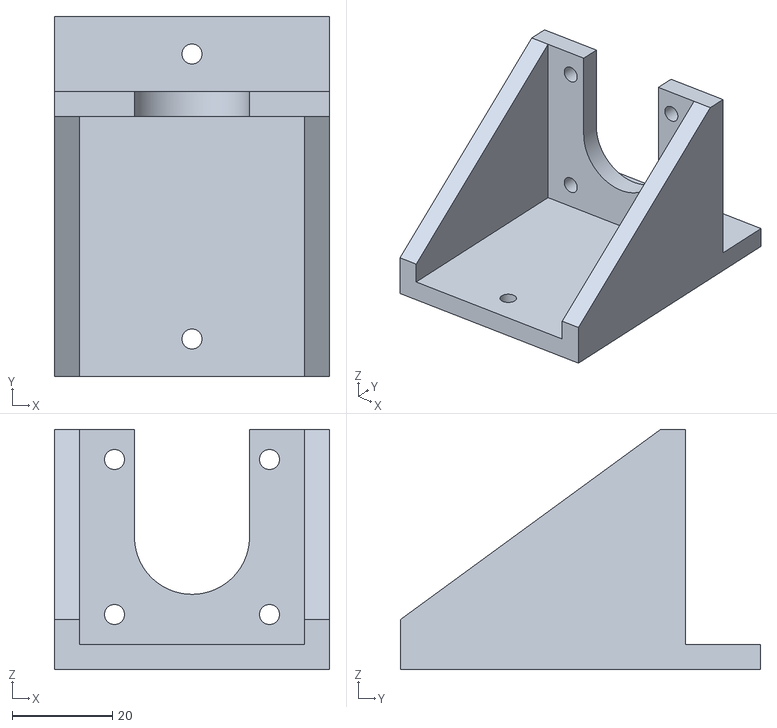
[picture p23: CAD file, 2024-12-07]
model/pump/motor_holder.stl
55.0 x 72.0 x 48.0

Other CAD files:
model/roller/Roller v3.step
model/spool/spool_guide.stl
model/pump/syring_holder.stl
model/pump/base_fix.stl
design tool/mold_simple.3dm

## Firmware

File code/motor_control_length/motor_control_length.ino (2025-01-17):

#include <Stepper.h>

// Define the number of steps for each motor
#define STEPS_PER_REV 200

// Create an instance of the Stepper class for the motor
Stepper stepper_motor(STEPS_PER_REV, 4, 5, 6, 7);

// Constants for lead screw and syringe dimensions
const float LEAD_SCREW_LEAD = 8.0; // Lead screw lead in mm (distance per rotation)
const float SYRINGE_DIAMETER = 26.5; // Syringe diameter in mm
const float NEEDLE_DIAMETER = 2.693; // Needle inner diameter in mm
const float EXTRUSION_MULTIPLIER = 1.3;

// Variables for dynamic speed control
unsigned long lastStepTime = 0;
float desiredRPM = 1.37; // Initial RPM for the motor

void setup()
{
  Serial.begin(9600);
  Serial.println("Enter the length (mm) to push:");
}

void loop()
{
  unsigned long currentTime = millis();

  // Check if there is serial input
  if (Serial.available() > 0)
  {
    // Wait for the complete input
    while (Serial.available() == 0) {}

    // Read the input length
    float lengthToPush = Serial.parseFloat();

    // Check if the input value is valid
    if (lengthToPush > 0)
    {
      float needleRadius = NEEDLE_DIAMETER / 2.0;
      float syringeRadius = SYRINGE_DIAMETER / 2.0;
      int stepsNeeded = (int)(lengthToPush * PI * needleRadius * needleRadius) / 
                        (PI * syringeRadius * syringeRadius) *
                        (STEPS_PER_REV / LEAD_SCREW_LEAD) * EXTRUSION_MULTIPLIER;

    // Calculate step delay based on desired RPM
    float stepDelay = (60.0 * 1000.0) / (STEPS_PER_REV * desiredRPM);
    
    // Control the motor to move the calculated steps
    for (int i = 0; i < stepsNeeded; i++)
    {
        // Move the motor one step at the desired speed
        if (currentTime - lastStepTime >= stepDelay) {
            stepper_motor.step(1);
            lastStepTime = currentTime;
        }
    
        // Update the current time
        currentTime = millis();
    }

      // Print the result to the serial monitor
      Serial.print("Length to push: ");
      Serial.print(lengthToPush);
      Serial.println(" mm");
      Serial.print("Steps needed: ");
      Serial.println(stepsNeeded);
      Serial.println("Enter the next length (mm) to push:");
    }
    else
    {
      Serial.println("Invalid input. Please enter a positive number.");
    }

    // Clear any remaining input buffer
    while (Serial.available() > 0)
    {
      Serial.read();
    }
  }
}

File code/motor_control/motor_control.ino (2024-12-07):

#include <Stepper.h>

// Define the number of steps for each motor
#define STEPS_LEFT 200
// #define STEPS_RIGHT 200
// #define STEPS_MANDREL 200

// Create instances of the Stepper class for each motor
Stepper stepper_left(STEPS_LEFT, 2, 3, 4, 5);
// Stepper stepper_right(STEPS_RIGHT, 6, 7, 8, 9);
// Stepper stepper_mandrel(STEPS_MANDREL, 10, 11, 12, 13);

// Variables to keep track of the last step time for each motor
unsigned long lastStepTimeLeft = 0;
// unsigned long lastStepTimeRight = 0;
// unsigned long lastStepTimeMandrel = 0;

// Variables for left motor speed control
float desiredRPMLeft = 0.2; // Initial RPM for left motor
float minRPMLeft = 0.1; // Minimum RPM for left motor
float maxRPMLeft = 5; // Maximum RPM for left motor

// Variables for right motor speed control
// float desiredRPMRight = 1; // Initial RPM for right motor
// float minRPMRight = 0.001; // Minimum RPM for right motor
// float maxRPMRight = 1; // Maximum RPM for right motor

// Variables for mandrel motor control
// float desiredRPMMandrel = 30;  // Set desired RPM for mandrel motor
// bool mandrelActive = false;    // Flag to control mandrel motor
// int mandrelDirection = -1;      // 1 for forward, -1 for reverse
// int stepsCount = 0;            // Steps counter for mandrel motor
// const int stepsPerTurn = STEPS_MANDREL / 8; // Steps per 1/8 turn

void setup()
{
  Serial.begin(9600);
}

void loop()
{
  unsigned long currentTime = millis();

  // Check for serial input
  // if (Serial.available() > 0) {
  //   char command = Serial.read();
  //   if (command == 's') {
  //     mandrelActive = true;
  //     lastStepTimeMandrel = currentTime;
  //   }
  //   else if (command == 'e') {
  //     mandrelActive = false;
  //   }
  // }

  // Read analog values from potentiometers
    int analogValueLeft = analogRead(A1);
  // int analogValueRight = analogRead(A0);

  // Map analog values to desired RPM ranges
  desiredRPMLeft = map(analogValueLeft, 0, 1023, minRPMLeft * 1000, maxRPMLeft * 1000) / 1000.0;
  // desiredRPMRight = map(analogValueRight, 0, 1023, minRPMRight * 1000, maxRPMRight * 1000) / 1000.0;

  // Calculate step delays for each motor
  float stepDelayLeft = (60.0 * 1000.0) / (STEPS_LEFT * desiredRPMLeft);
  // float stepDelayRight = (60.0 * 1000.0) / (STEPS_RIGHT * desiredRPMRight);
  // float stepDelayMandrel = (60.0 * 1000.0) / (STEPS_MANDREL * desiredRPMMandrel);  // Use desiredRPMMandrel for mandrel

  // Control Right Motor
  // if (currentTime - lastStepTimeRight >= stepDelayRight) {
  //   int stepsToTakeRight = (currentTime - lastStepTimeRight) / stepDelayRight;
  //   stepper_right.step(stepsToTakeRight);
  //   lastStepTimeRight = currentTime;
  // }

  // Control Left Motor
  if (currentTime - lastStepTimeLeft >= stepDelayLeft) {
    int stepsToTakeLeft = (currentTime - lastStepTimeLeft) / stepDelayLeft;
    stepper_left.step(-stepsToTakeLeft);
    lastStepTimeLeft = currentTime;
  }

  // Control Mandrel Motor if the command was received
  // if (mandrelActive) {
  //   if (currentTime - lastStepTimeMandrel >= stepDelayMandrel) {
  //     int stepsToTakeMandrel = (currentTime - lastStepTimeMandrel) / stepDelayMandrel;
  //     stepper_mandrel.step(mandrelDirection * stepsToTakeMandrel);
  //     lastStepTimeMandrel = currentTime;

  //     stepsCount += stepsToTakeMandrel;
      
  //     // If mandrel has completed 1/8 turn
  //     if (stepsCount >= stepsPerTurn) {
  //       stepsCount = 0; // Reset the steps counter
  //       mandrelDirection *= -1; // Reverse direction

  //       // Pause for 1 second after completing 1/8 turn
  //       delay(2000);
  //       currentTime = millis();
  //       lastStepTimeMandrel = currentTime;
  //     }
  //   }
  // }
}

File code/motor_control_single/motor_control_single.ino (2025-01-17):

#include <Stepper.h>

// Define the number of steps for each motor
#define STEPS 200

// Create instances of the Stepper class for each motor
Stepper stepper(STEPS, 4, 5, 6, 7);

// Variables to keep track of the last step time for each motor
unsigned long lastStepTime = 0;

// Variables for left motor speed control
float desiredRPM = 1.37; // Initial RPM for left motor
float minRPM = 0.1; // Minimum RPM for left motor
float maxRPM = 5; // Maximum RPM for left motor

void setup()
{
  Serial.begin(9600);
}

void loop()
{
  unsigned long currentTime = millis();

  // Read analog values from potentiometers
  int analogValue = analogRead(A0);

  // Map analog values to desired RPM ranges
  desiredRPM = map(analogValue, 0, 1023, minRPM * 1000, maxRPM * 1000) / 1000.0;

  // Calculate step delays for each motor
  float stepDelay = (60.0 * 1000.0) / (STEPS * desiredRPM);

  // Control Left Motor
  if (currentTime - lastStepTime >= stepDelay) {
    // int stepsToTakeLeft = (currentTime - lastStepTime) / stepDelay;
    // stepper.step(-stepsToTakeLeft);
    stepper.step(1);
    lastStepTime = currentTime;
  }
}

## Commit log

2024-12-07 arduino code
2024-12-11 optical model
    [light_sensor_cap.stl]

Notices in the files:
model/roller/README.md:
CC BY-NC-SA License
